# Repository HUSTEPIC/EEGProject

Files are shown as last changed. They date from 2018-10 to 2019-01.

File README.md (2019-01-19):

# EEGProject

+ 用于脑电信号研究的采集装置；
+ **国家重点研发计划项目启动会** “抑郁症复发的预警体系建立和综合干预策略研究“
+ “基于机器学习和云计算的抑郁症服务平台的研发和应用”方案介绍

## EEG_V2.1
1. ads1299参考电压有4.5V；
    + 原因：SPI的DIN通信线上有电阻，导致CH559T的SPI通信没有成功。
2. CH559T 的USB_Hub,前几次能检测到设备，没有找到原因。
    + 增加AMS1117-5v稳压模块，还是没能解决问题；
## EEG_V3.0
1. 制作22路的电极帽
     + ADS1299 - 6 四块构成24路的参考电极帽
2. 主控CH559L
3. 焊接成功
    + 参考电压输出4.5V；
    + 级联第一步测试成功，还需要对SPI进行测试
4. 供电方式
    + 采用纽扣电池进行供电
    + 通过两个开关控制供电和充电
## EEGChargeBattery
1. 纽扣电池进行供电。
2. 设计的可充电回路。
3. 通过开关控制串联供电和并联充电

## EEG_V4.0[2018.12.27]

1. 修改CH559L--CC2540模块

2. 添加12*2排母孔
   + 用于CC2540主控的连接；
   + PCB布局的距离控制；
   + 制作一个模块就行

3. 添加3.3v稳压电压模块
   + CC2540需要
   + ADS1299需要

4. 布设了基本的SPI信号线

   + 后面查找其它信号线相关的连接

5. 引出SPI信号接口，用作CC-Debug

6. 引出GPIO口，用于其余信号的控制

7. 两个USB接口

   + 两颗纽扣电池需要进行，串联供电，并联充电

   + 因此电池充电的时候，不能提供电源进行工作
   + 所以 USB_1,充电；USB_2 DM,DP功能

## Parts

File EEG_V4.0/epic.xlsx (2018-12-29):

Comment | Description | LibRef | Quantity | 单价 | 价格
包装一：之前已经确定
105K16V | 贴片电 | C0603X7R-105K16V | 50 | 0.1 | 5
104K50V | 贴片电 | C0603X7R-104K50V | 50 | 0.1 | 5
102K10V | 贴片电 | C0603X7R-102K10V | 50 | 0.1 | 5
106K50V | 贴片电 | C0603X7R-106K50V | 50 | 0.1 | 5
475K16V | 贴片电 | C0603X7R-475K16V | 20 | 0.1 | 2
100Uf | C1210-100UF | C1210钽电容 --100UF--B3 | 20 | 0.9 | 18
LED0603G | 贴片二极 | DLED-0603-G | 50 | 0.05 | 2.5
ESDA_TR1/0603 | Zener Diode | D Zener | 20 | 0.5 | 10
500mA/13.2V | 500mA/13.2V 自恢复 | 1206MSD | 10 | 0.5 | 5
22RF | 贴片电 | R0603-22RF | 100 | 0.05 | 5
3KF | 贴片电 | R0603-3KF | 100 | 0.05 | 5
470RF | 贴片电 | R0603-470RF | 100 | 0.05 | 5
AMS1117_5V | AMS1117_5V | AMS1117-5V | 10 | 0.1 | 1
TPD4E1B06 | ESD-防静 | U-TPD4E1B06 | 50 | 2 | 100
AMS1117_3.3V | AMS1117_3.3V | AMS1117-3.3V | 10 | 0.1 | 1
 |  |  |  |  | 174.5
包装二：两个包装分开装
100pF | C-EU0603-RND | C0603-ROUND | 50 | 0.1 | 5
1uF | C-EU0603-RND | C0603-ROUND | 50 | 0.1 | 5
22p | C-EU0603-RND | C0603-ROUND | 50 | 0.1 | 5
2.7M | R-EU_R0603 | R0603-ROUND | 100 | 0.05 | 5
1M | R-EU_R0603 | R0603-ROUND | 100 | 0.05 | 5
910K | 910K | R0603-ROUND | 100 | 0.05 | 5
10K | R-EU_R0603 | R0603 | 100 | 0.05 | 5
4.7K | RESISTOR0603- | RES 0603-RES | 100 | 0.05 | 5
1K | R-EU_R0603 | R0603 | 100 | 0.05 | 5
330R | RESISTOR0603-RES | 0603-RES | 100 | 0.05 | 5
5R1 | RESISTOR0603-RES | 0603-RES | 100 | 0.05 | 5
10uH | L-EUL3216C | L3216C | 20 | 0.1 | 2
16MHz | XTAL/S | QS | 10 | 0.3 | 3
1N5819-B | 1N5819-B | DO41-7.6 | 10 | 0.1 | 1
 |  |  |  |  | 61

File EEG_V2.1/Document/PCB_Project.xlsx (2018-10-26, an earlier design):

Comment | Description | Designator | Footprint | LibRef | Quantity
105K16V | 贴片电容-陶瓷 | C1, C3, C5, C14, C16, C17, C20, C23 | C0603 | C0603X7R-105K16V | 8
104K50V | 贴片电容-陶瓷 | C2, C18, C21, C22, C26, C29 | C0603 | C0603X7R-104K50V | 6
101K10V | 贴片电容-陶瓷 | C6, C7 | C0603 | C0603X7R-101K10V | 2
100Uf | C1210-100UF | C15 | C1210 | C1210钽电容 --100UF--B3528 | 1
106K50V | 贴片电容-陶瓷 | C19, C24, C31 | C0603 | C0603X7R-106K50V | 3
103K50V | 贴片电容-陶瓷 | C30, C33 | C0603 | C0603X7R-103K50V | 2
152K16V | 贴片电容-陶瓷 | C32 | C0603 | C0603X7R-152K16V | 1
LED0603G | 贴片二极管-LED | D1 | D-LED0603G | DLED-0603-G | 1
ESDA_TR1/0603 | Zener Diode | D2, D4 | HS_0603D | D Zener | 2
SMAJ5.0CA |  | D3 | DO-214 | SMAJ5.0CA | 1
J-D2.45-1*4 | J-D2.45-1*4 | J1 | D2.54-1*4P | J-D2.54-1*4单排排母 | 1
C-DSUB-25 | C-DSUB-0064 | J3 | C-DSUB-25 | C-DSUB-25 | 1
USB-MINI-SOCKET | USB-A卧式插座 | J4 | MICRO-USB - 5.9 | J-USB-MINI-SOCKET | 1
J-D2.54-1*2 | J-D2.54-1*2 | J5 | D2.54-1*2P | J-D2.54-1*2单排 | 1
SS-12D00 | SS-12D00 | K1 | SS-12D00 | SS-12D00(1P2T) 立式 柄高5MM | 1
10uH | 贴片电感-层叠 | L1 | L0805 | L-0805-10uH | 1
ADS1299 | ADS1299-S-PQFP-64 | M1 | ADS1299-TSQFP50P1200X1200X105-64N | ADS1299 | 1
PHONE |  | P |  | PHONE | 1
22RF | 贴片电阻-通用 | R5, R7 | R0603 | R0603-22RF | 2
10KF | 贴片电阻-通用 | R6, R8, R9, R10, R11, R13, R16, R17, R18, R19, R20 | R0603 | R0603-10KF | 11
2KF | 贴片电阻-通用 | R12 | R0603 | R0603-2KF | 1
1MF | 贴片电阻-通用 | R14 | R0603 | R0603-1MF | 1
0R | 贴片电阻-通用 | R15, R21 | R0603 | R0603-0R | 2
1KF | 贴片电阻-通用 | R22, R23, R24, R25 | R0603 | R0603-1KF | 4
1RJ | 贴片电阻-通用 | R26 | R0603 | R0603-1RJ | 1
2*3*0.65 | 薄膜按键 | S1 | S-K2*3 - duplicate | 2*3*0.65 薄膜按键 | 1
CH559T | usb通信 | U1 | TSSOP20 | CH559T | 1

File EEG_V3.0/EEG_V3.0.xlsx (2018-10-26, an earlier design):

Comment | Description | Footprint | LibRef | Quantity |  | 总价
105K16V | 贴片电容-陶瓷 | C0603 | C0603X7R-105K16V | 100 | 0.2 | 20
104K50V | 贴片电容-陶瓷 | C0603 | C0603X7R-104K50V | 100 | 0.2 | 20
TPD4E1B06 | ESD-防静电干扰 | U-ESD-DRL-SOTFL50P160X60-6N | U-TPD4E1B06 | 30 | 1.8 | 54
102K10V | 贴片电容-陶瓷 | C0603 | C0603X7R-102K10V | 100 | 0.2 | 20
2.2KF | 贴片电阻-通用 | R0603 | R0603-2.2KF | 1000 | 0.008 | 8
CH559T | 芯片 | SSOP-20 |  | 10 | 10 | 100
Micro USB插座母座 Micro5p/F 插脚5.9 带定位柱 有卷边 |  |  |  | 100 | 0.1 | 10
 |  |  |  |  |  |  | 232

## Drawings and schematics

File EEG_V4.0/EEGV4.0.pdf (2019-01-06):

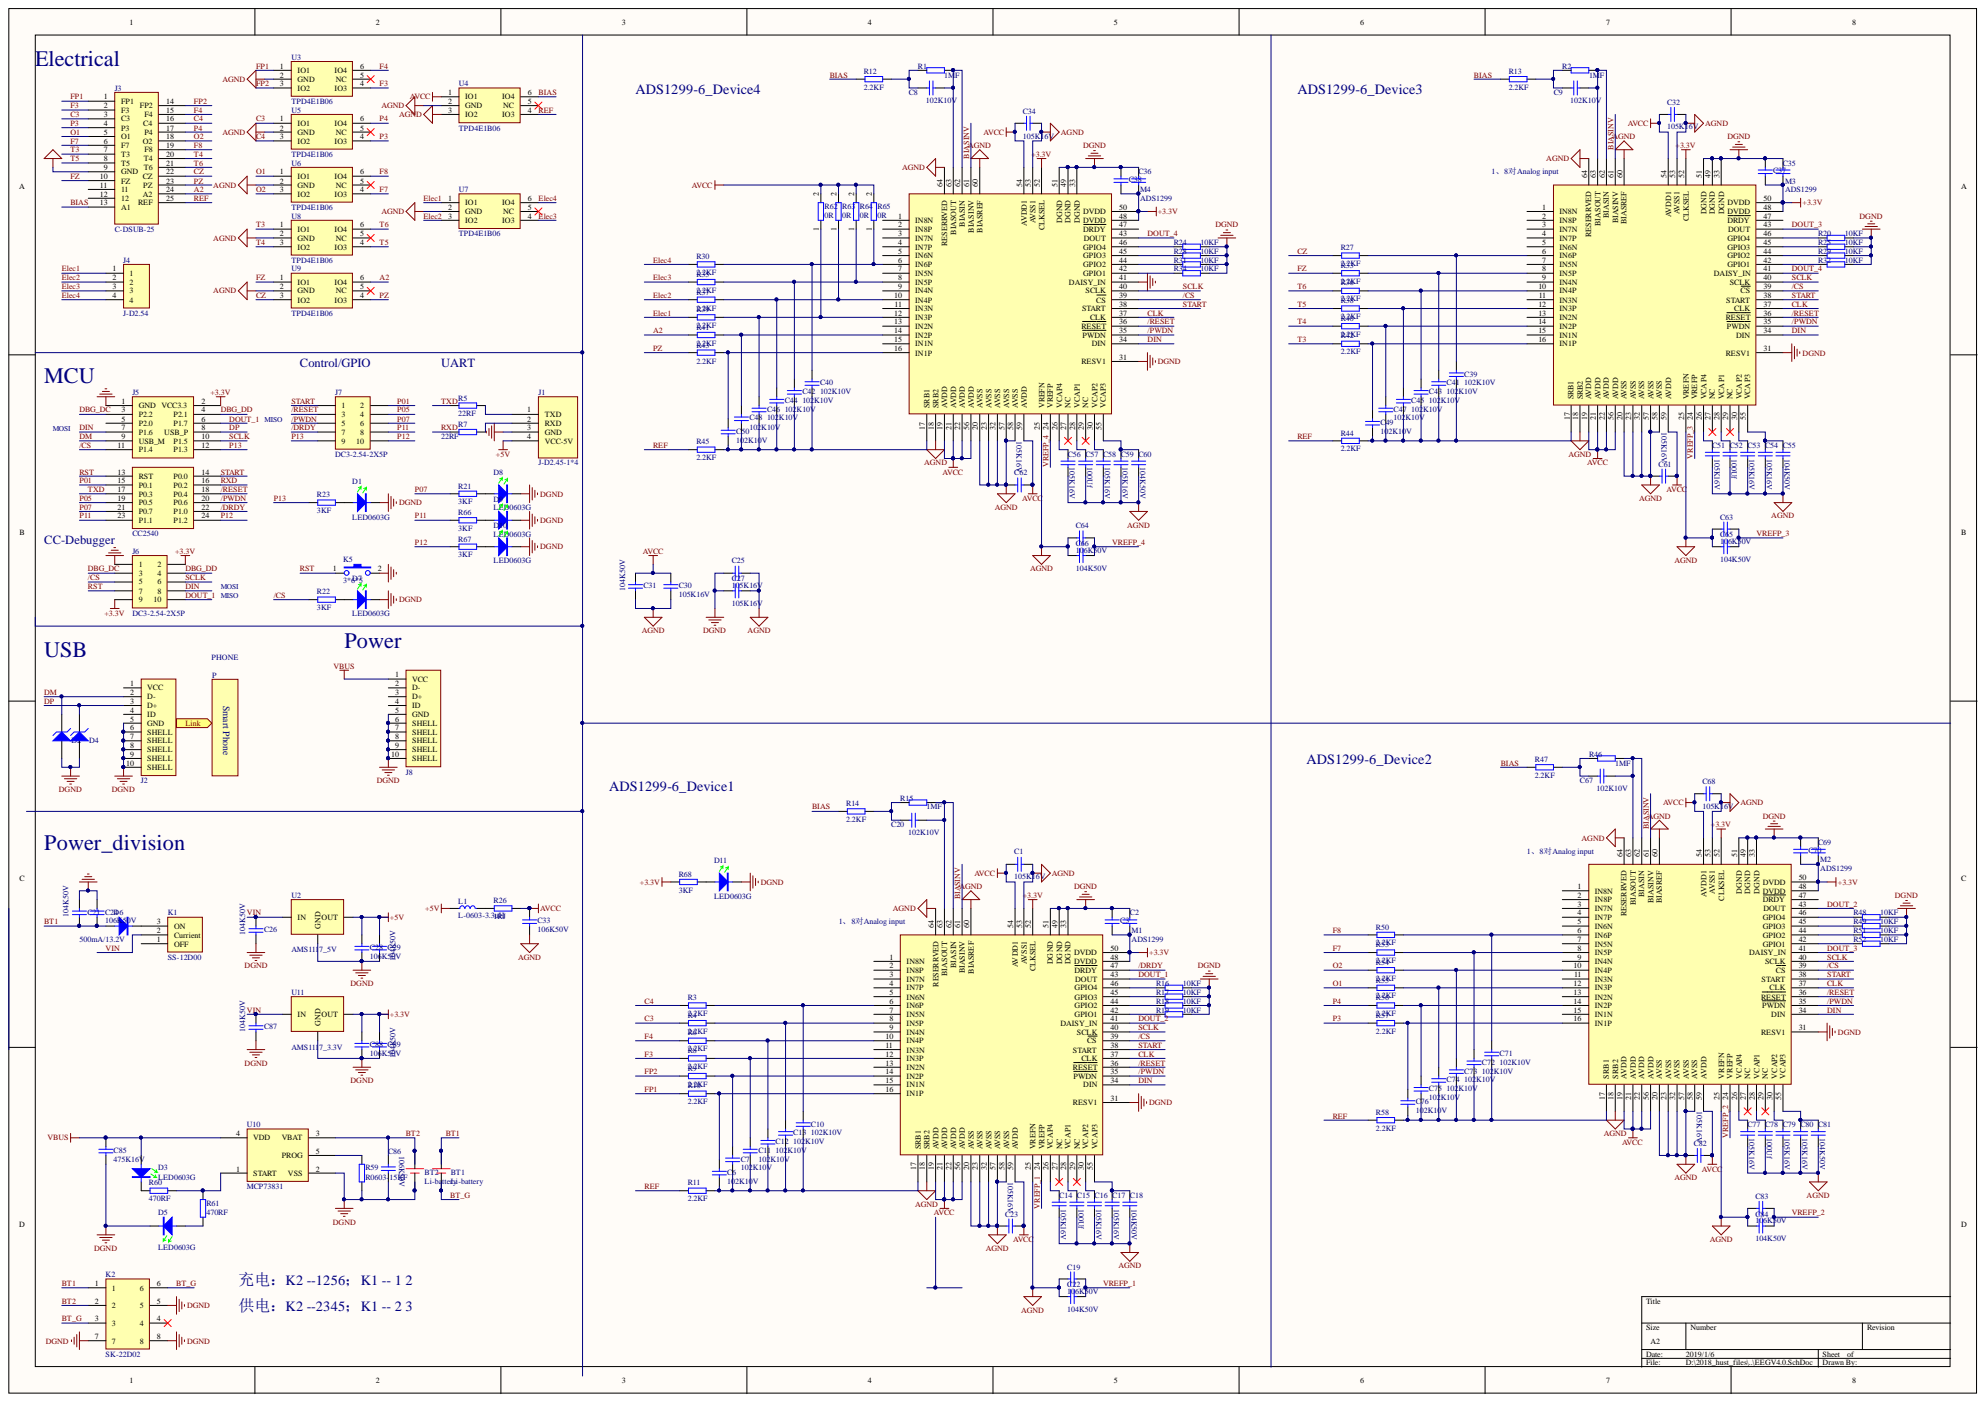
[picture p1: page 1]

BIASREF 60 BIASINV 61 BIASIN 62 BIASOUT 63 RESERRVED 64

Comment | Description | Designator | Footprint | LibRef | Quantity
Li-battery | 纽扣电池LIR2023 | BT1, BT2 | LIR2032 | Li-batttery | 2
105K16V | 贴片电容-陶瓷 | C1, C3, C14, C16, C17, C23, C25, C27, C30, C32, C34, C37, C38, C51, C53, C54, C56, C58, C59, C61, C62, C68, C70, C77, C79, C80, C82 | C0603 | C0603X7R-105K16V | 27
104K50V | 贴片电容-陶瓷 | C2, C18, C21, C22, C26, C29, C31, C35, C36, C55, C60, C65, C66, C69, C81, C84, C87, C89 | C0603 | C0603X7R-104K50V | 18
102K10V | 贴片电容-陶瓷 | C6, C7, C8, C9, C10, C11, C12, C13, C20, C39, C40, C41, C42, C43, C44, C45, C46, C47, C48, C49, C50, C67, C71, C72, C73, C74, C75, C76 | C0603 | C0603X7R-102K10V | 28
100Uf | C1210-100UF | C15, C52, C57, C78 | C1210 | C1210钽电容 --100UF--B3528 | 4
106K50V | 贴片电容-陶瓷 | C19, C24, C28, C33, C63, C64, C83, C86, C88 | C0603 | C0603X7R-106K50V | 9
475K16V | 贴片电容-陶瓷 | C85 | C0603 | C0603X7R-475K16V | 1
LED0603G | 贴片二极管-LED | D1, D3, D5, D7, D8, D9, D10, D11 | D-LED0603G | DLED-0603-G | 8
ESDA_TR1/0603 | Zener Diode | D2, D4 | HS_0603D | D Zener | 2
500mA/13.2V | 500mA/13.2V 自恢 复保险丝 | D6 | D1206 | 1206MSD | 1
J-D2.45-1*4 | J-D2.45-1*4 | J1 | D2.54-1*4P | J-D2.54-1*4单排排 母 | 1
USB-MINI-SOCKET | USB-A卧式插座 | J2, J8 | MICRO-USB - 5.9 | J-USB-MINI-SOCKET | 2
C-DSUB-25 | C-DSUB-0064 | J3 | C-DSUB-25 | C-DSUB-25 | 1
J-D2.54 | 单排排针 | J4 | D2.54-1*4P | J-D2.54-1*4-单排 | 1
CC2540 | 蓝牙主控模块的接 口 | J5 | CC2540 | CC2540 | 1
DC3-2.54-2X5P | 简牛插座-直针 | J6, J7 | DC3-2.54-2X5P | J-DC3-2.54-2X5P | 2
SS-12D00 | SS-12D00 | K1 | SS-12D00 | SS-12D00(1P2T) 立 式 柄高5MM | 1
SK-22D02 | 波动开关-2档6脚 | K2 | SK-22D02 | SK-22D02 | 1
3*6*5 | 贴片-卧式轻触开关 | K5 | S-K3*6 | 3*6*5 | 1
L-0603-3.3uH | 贴片电感-屏蔽 | L1 | L0603 | L-0603-3.3uH | 1
ADS1299 | ADS1299-S-PQFP-64 | M1, M2, M3, M4 | ADS1299-TSQFP50P1200X12 00X105-64N | ADS1299 | 4
PHONE | | P | | PHONE | 1
1MF | 贴片电阻-通用 | R1, R2, R15, R46 | R0603 | R0603-1MF | 4
2.2KF | 贴片电阻-通用 | R3, R4, R6, R8, R9, R10, R11, R12, R13, R14, R27, R30, R33, R35, R36, R37, R38, R39, R40, R41, R42, R43, R44, R45, R47, R50, R53, R54, R55, R56, R57, R58 | R0603 | R0603-2.2KF | 32
22RF | 贴片电阻-通用 | R5, R7 | R0603 | R0603-22RF | 2
10KF | 贴片电阻-通用 | R16, R17, R18, R19, R20, R24, R25, R28, R29, R31, R32, R34, R48, R49, R51, R52 | R0603 | R0603-10KF | 16
3KF | 贴片电阻-通用 | R21, R22, R23, R66, R67, R68 | R0603 | R0603-3KF | 6
1RJ | 贴片电阻-通用 | R26 | R0603 | R0603-1RJ | 1
R0603-15KF | 贴片电容-通用 | R59 | R0603 | R0603-15KF | 1
470RF | 贴片电阻-通用 | R60, R61 | R0603 | R0603-470RF | 2
0R | 贴片电阻-通用 | R62, R63, R64, R65 | R0603 | R0603-0R | 4
AMS1117_5V | AMS1117_5V | U2 | SOT-223 | AMS1117-5V | 1
TPD4E1B06 | ESD-防静电干扰 | U3, U4, U5, U6, U7, U8, U9 | U-ESD-DRL-SOTFL50P160X60-6N | U-TPD4E1B06 | 7
MCP73831 | charge IC | U10 | SOT23-5N | MCP73831 | 1
AMS1117_3.3V | AMS1117_3.3V | U11 | SOT-223 | AMS1117-3.3V | 1

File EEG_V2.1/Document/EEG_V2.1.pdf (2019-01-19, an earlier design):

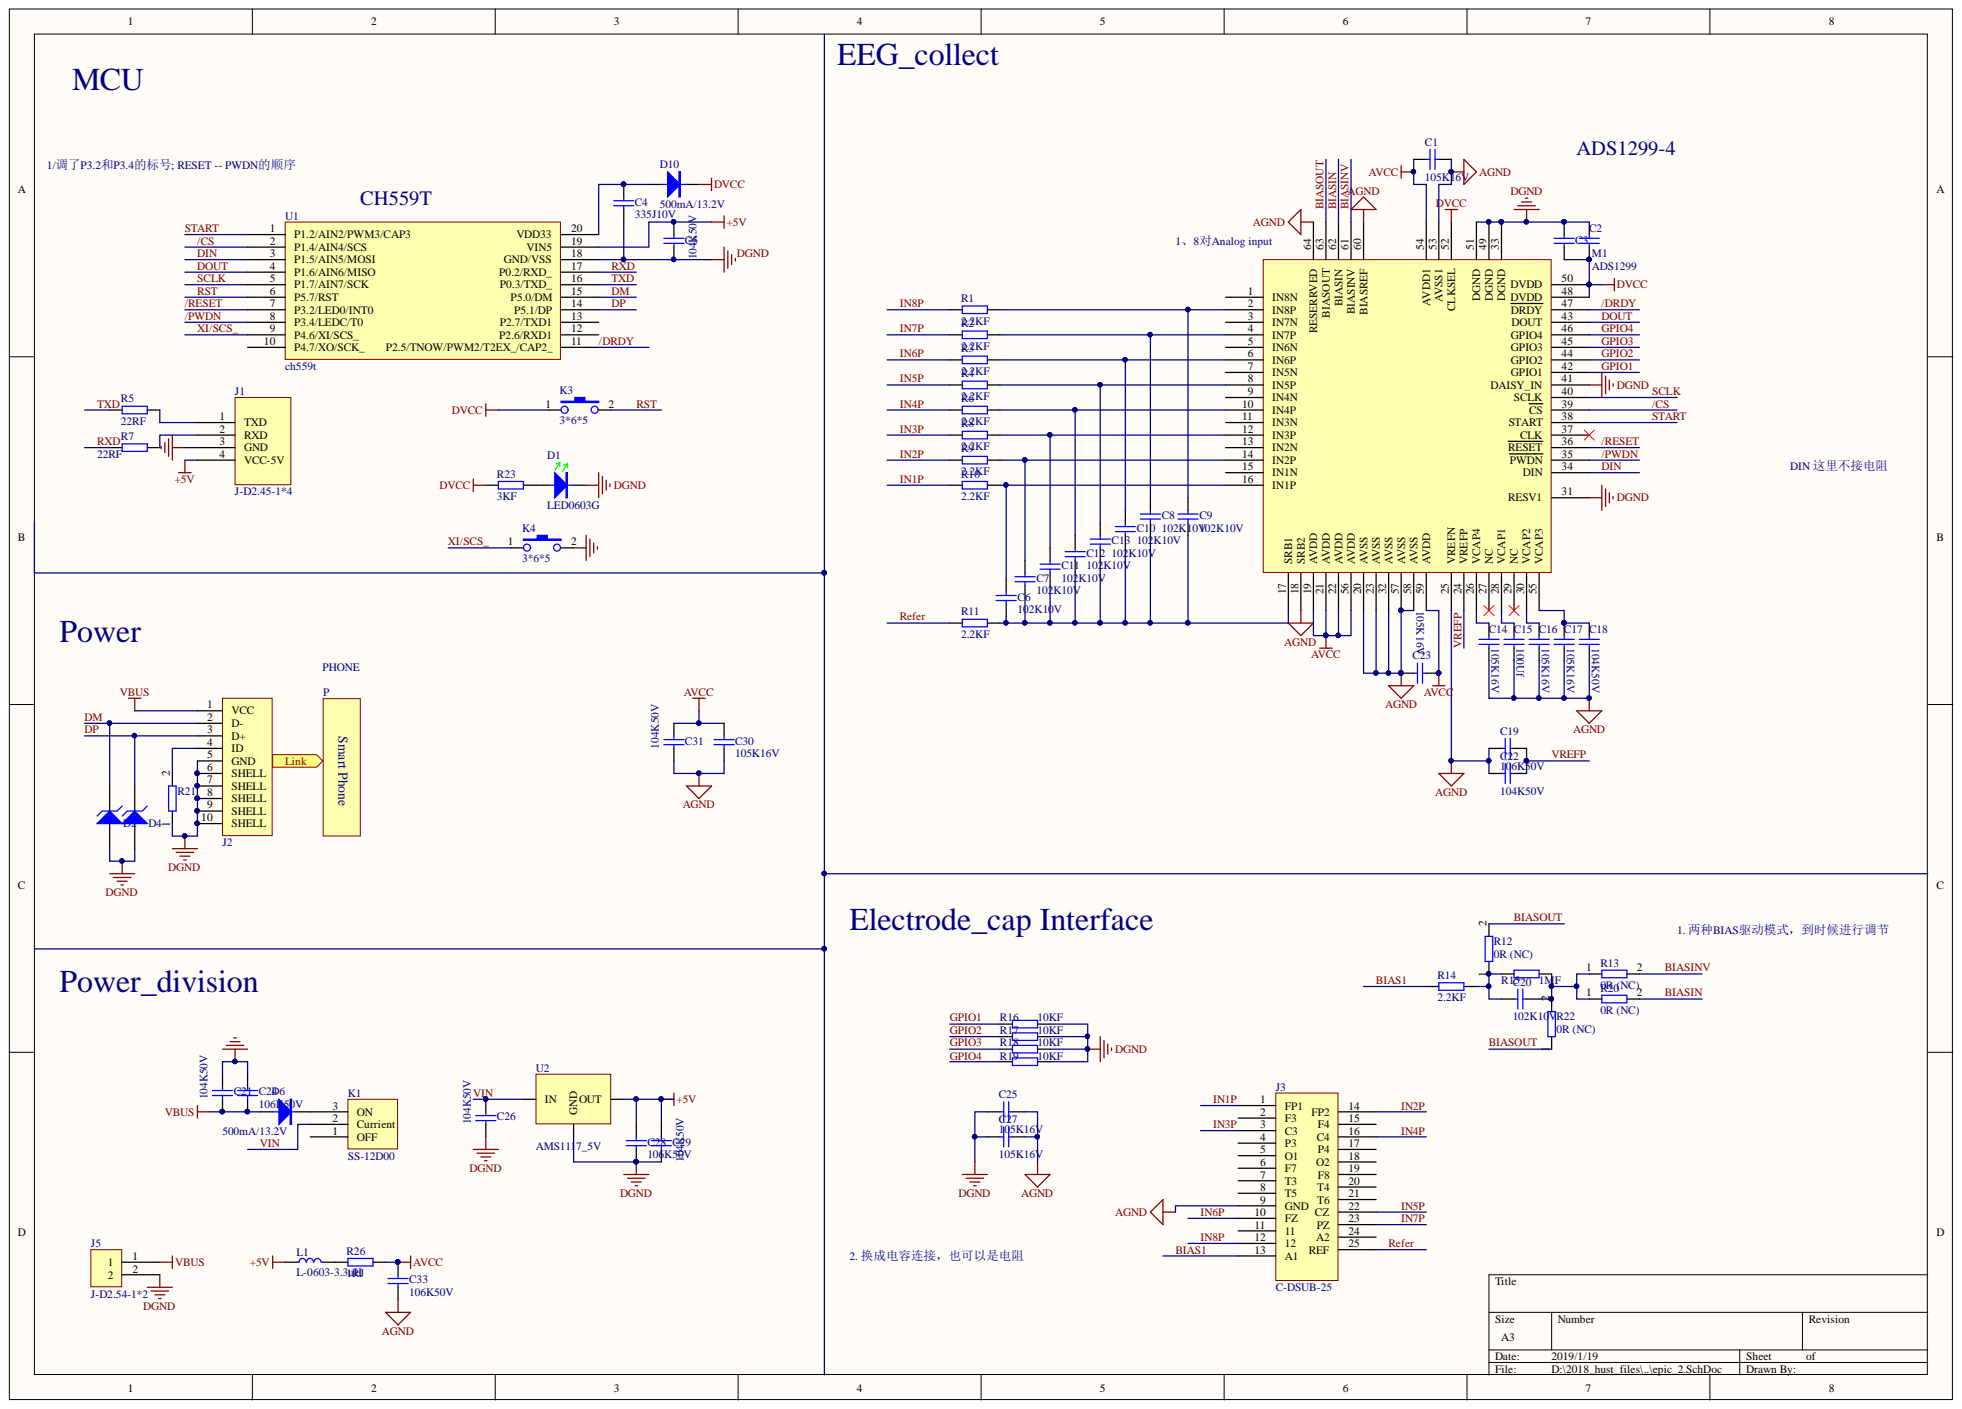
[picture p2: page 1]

BIASREF 60 BIASINV 61 BIASIN 62 BIASOUT 63 RESERRVED 64

P3.4/LEDC/T0 8 | /DRDY | | | IN7N 3

D+ 3
ID 4
GND 5

SHELL 7

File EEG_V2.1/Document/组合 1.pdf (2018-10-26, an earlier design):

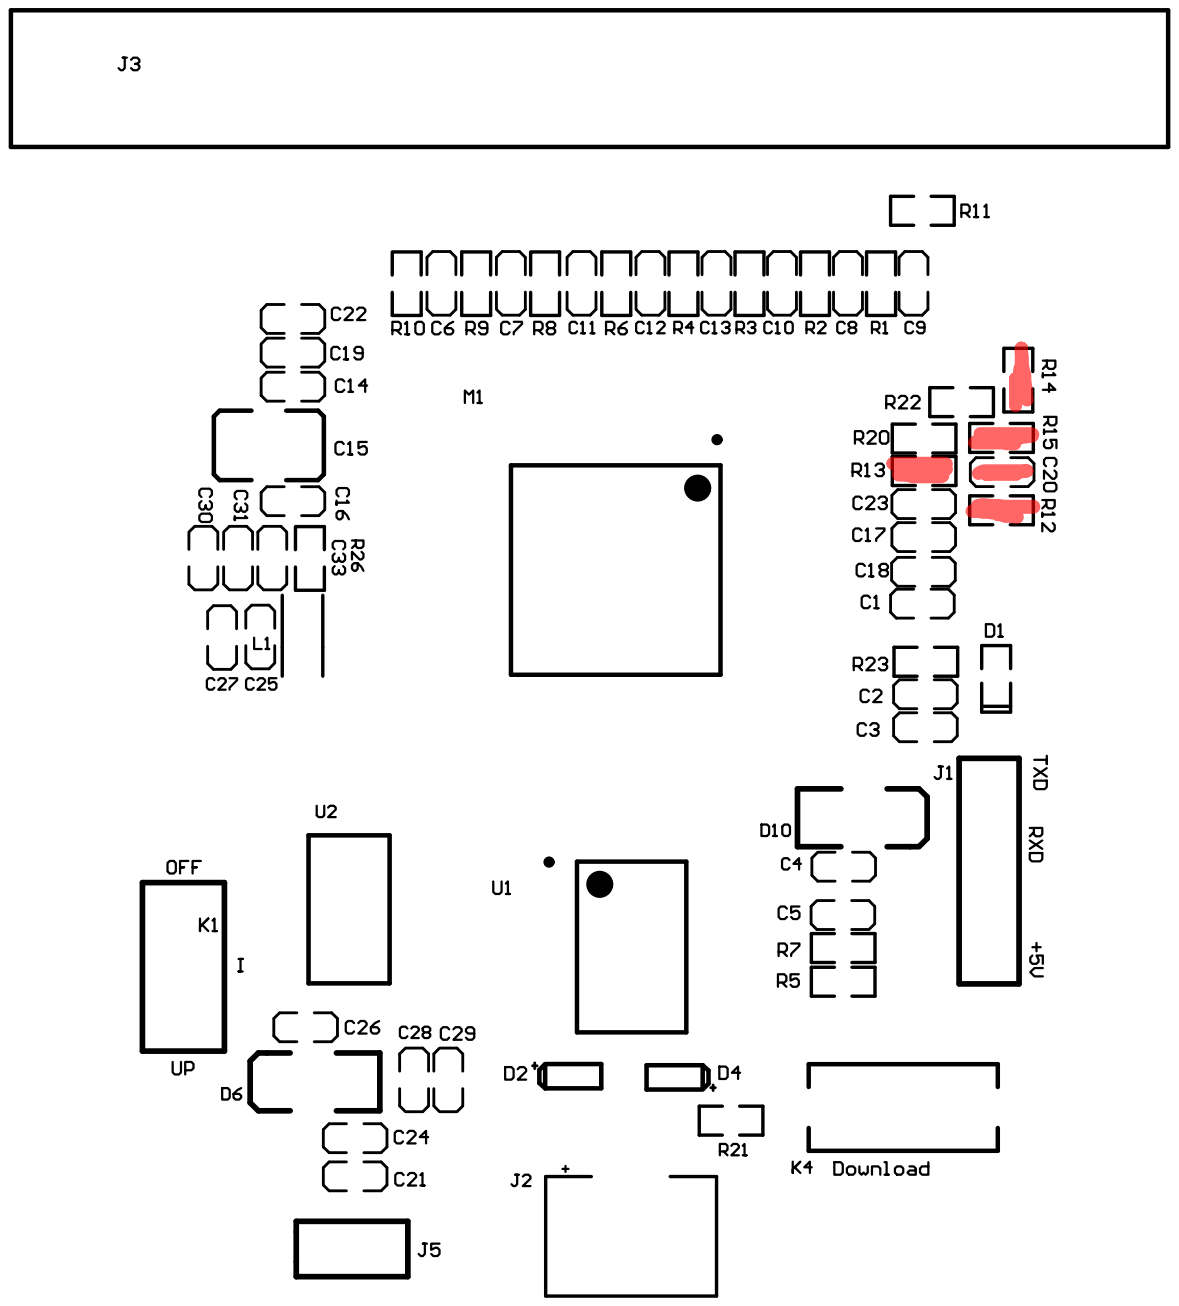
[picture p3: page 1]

Comment | Description | Designator | Footprint | LibRef | Quantity
105K16V | 贴片电容-陶瓷 | C1, C3, C14, C16, C17, C23, C25, C27, C30 | C0603 | C0603X7R-105K16V | 9
104K50V | 贴片电容-陶瓷 | C2, C5, C18, C21, C22, C26, C29, C31 | C0603 | C0603X7R-104K50V | 8
335J10V | 贴片电容-陶瓷 | C4 | C0603 | C0603X7R-335J10V | 1
102K10V | 贴片电容-陶瓷 | C6, C7, C8, C9, C10, C11, C12, C13, C20 | C0603 | C0603X7R-102K10V | 9
100Uf | C1210-100UF | C15 | C1210 | C1210钽电容 --100UF--B3528 | 1
106K50V | 贴片电容-陶瓷 | C19, C24, C28, C33 | C0603 | C0603X7R-106K50V | 4
LED0603G | 贴片二极管-LED | D1 | D-LED0603G | DLED-0603-G | 1
ESDA_TR1/0603 | Zener Diode | D2, D4 | HS_0603D | D Zener | 2
500mA/13.2V | 500mA/13.2V 自恢复保险丝 D6, D10 | | D1206 | 1206MSD | 2
J-D2.45-1*4 | J-D2.45-1*4 | J1 | D2.54-1*4P | J-D2.54-1*4单排排母 | 1
USB-MINI-SOCKET | USB-A卧式插座 | J2 | MICRO-USB - 5.9 | J-USB-MINI-SOCKET | 1
C-DSUB-25 | C-DSUB-0064 | J3 | C-DSUB-25 | C-DSUB-25 | 1
J-D2.54-1*2 | J-D2.54-1*2 | J5 | D2.54-1*2P | J-D2.54-1*2单排 | 1
SS-12D00 | SS-12D00 | K1 | SS-12D00 | SS-12D00(1P2T) 立式 | 1
3*6*5 | 贴片-卧式轻触开关 | K3, K4 | S-K3*6 | 3*6*5 | 2
L-0603-3.3uH | 贴片电感-屏蔽 | L1 | L0603 | L-0603-3.3uH | 1
ADS1299 | ADS1299-S-PQFP-64M1 | | ADS1299-TSQFP50P1200X1200X105-64N ADS1299 | | 1
PHONE | | P | | PHONE | 1
2.2KF | 贴片电阻-通用 | R1, R2, R3, R4, R6, R8, R9, R10, R11, R14 | R0603 | R0603-2.2KF | 10
22RF | 贴片电阻-通用 | R5, R7 | R0603 | R0603-22RF | 2
0R (NC) | 贴片电阻-通用 | R12, R13, R20, R22 | R0603 | R0603-0R | 4
1MF | 贴片电阻-通用 | R15 | R0603 | R0603-1MF | 1
10KF | 贴片电阻-通用 | R16, R17, R18, R19 | R0603 | R0603-10KF | 4
0R | 贴片电阻-通用 | R21 | R0603 | R0603-0R | 1
3KF | 贴片电阻-通用 | R23 | R0603 | R0603-3KF | 1
1RJ | 贴片电阻-通用 | R26 | R0603 | R0603-1RJ | 1
ch559t | CH559T-20pin | U1 | SSOP-20 | CH559T | 1
AMS1117_5V | AMS1117_5V | U2 | SOT-223 | AMS1117-5V | 1

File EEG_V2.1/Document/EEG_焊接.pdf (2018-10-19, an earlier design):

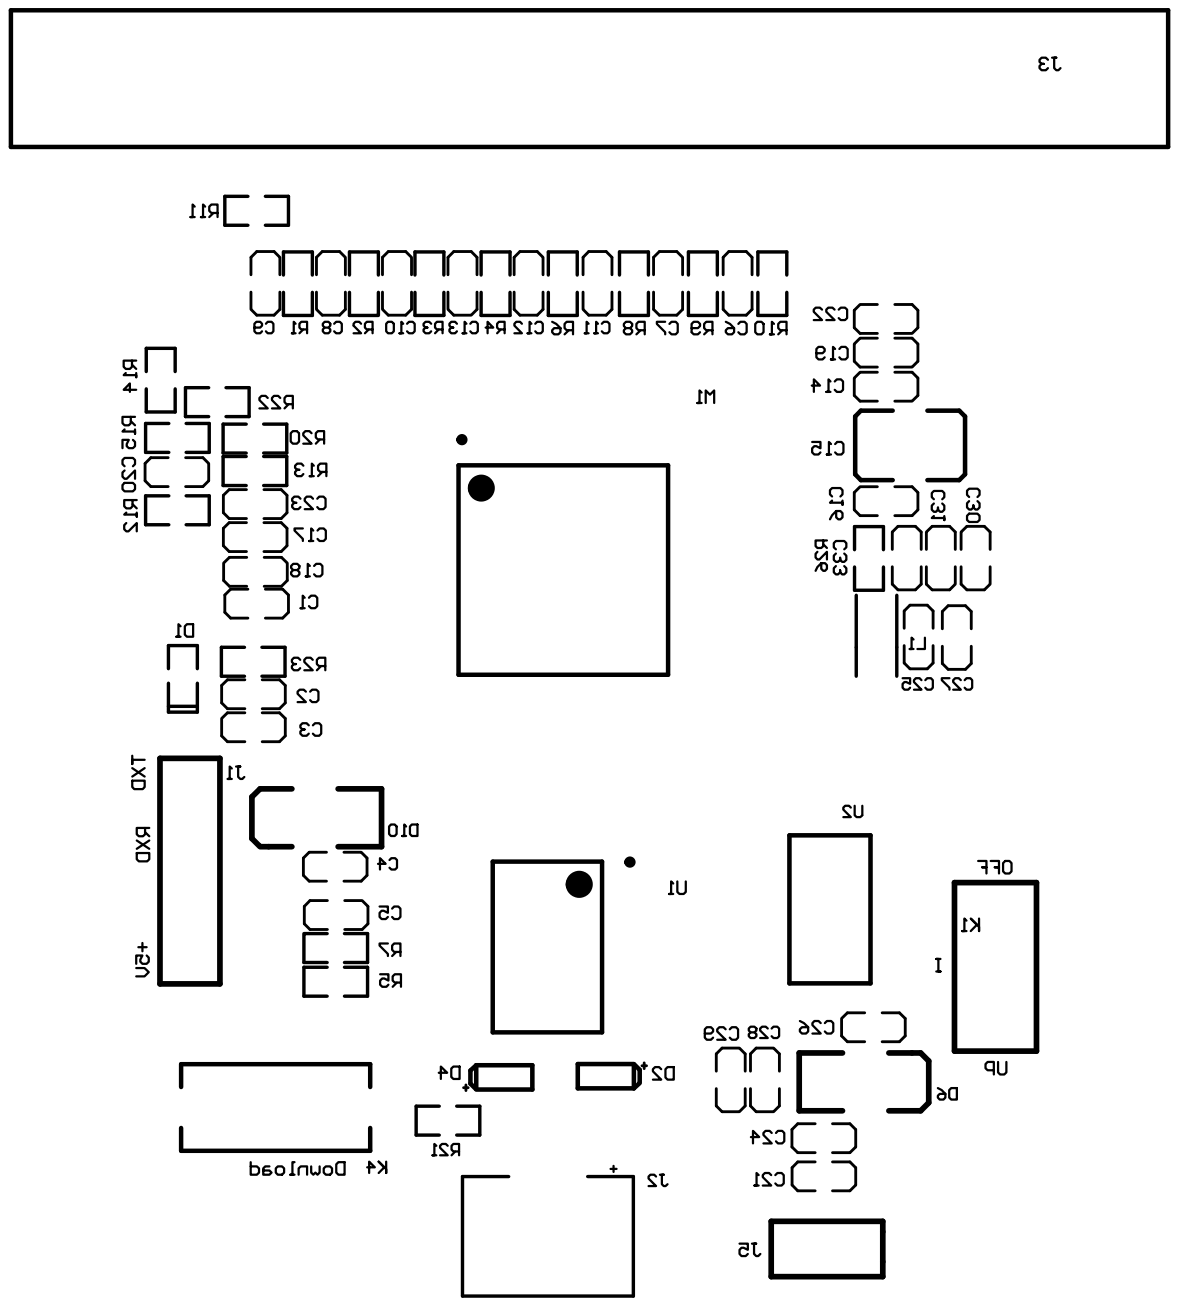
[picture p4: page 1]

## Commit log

2018-10-17 This is EEG V1.0. Using CH559l-40pin.
    [EPIC.SCHLIB, PCB_Project.PrjPcb, epic.PcbDoc, epic.PcbLib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]
2018-10-18 This is EEG_V2.0. Because PCB's wiring have some question. Destory IC chip
    [EPIC.SCHLIB, PCB_Project.PrjPcb, PCB_Project.xlsx, epic.PcbDoc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]
2018-10-18 This is EEG_V2.1. Rewring plane. Protecting IC_chip.
    [PCB_Project.PrjPcb, PCB_Project.xlsx, epic.SchLib, epic2.PcbDoc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]
2018-10-19 Change the EEG. Making is same with EEGv1.0
    [PCB_Project.PrjPcb, epic2.GBL, epic2.GBO, epic2.GBP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]
2018-10-19 EEGV2_1 change SCH. It delete some nnecessary things.
    [EEGV2.1.PcbLib, EEGV2.1.SCHLIB, PCB_Project.PrjPcb, epic.SchLib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]
2018-10-26 This ads1299 have the vref 4.5v. The mistake is SPI design . Having a resistance.
    [PCB_Project.PrjPcb, PCB_Project.xlsx, epic2.PcbDoc, epic_2.SchDoc]
2018-10-26 EEG3.0 first
    [EEGV3.0.PcbDoc, EEGV3.0.PcbLib, EEGV3.0.SCHLIB, EEGV3.0.SchDoc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]
2018-10-30 Achieving the EEG_V3.0 project. It is 23 load.
    [EEGV3.0.SchDoc, EEG_V3.0.PrjPcb]
2018-11-06 EEG_V3.0 TEST Sucessful
    [EEGV3.0.SchDoc, EEG_V3.0.PrjPcb]
2018-11-29 add eegChargeBattery
    [charge battery.PrjPcb, charge_battery.PcbDoc, charge_battery.PcbLib, charge_battery.SCHLIB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]
2018-12-26 CH-X change to cc2540
    [EEGV4.0.PcbLib, EEGV4.0.SCHLIB, EEGV4.0.SchDoc, EEG_V4.0.PrjPcb]
2019-01-19 add pdf document
    [EEG_V3.0.PrjPcb, PCB_Project.PrjPcb, PCB_Project.xlsx]
